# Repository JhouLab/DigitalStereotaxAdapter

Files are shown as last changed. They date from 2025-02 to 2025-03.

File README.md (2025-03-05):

Ridiculously cheap (and functional) 3-axis digital stereotax adapter
============================================

<div align="center">
<video src="https://github.com/user-attachments/assets/23dbc953-8d90-421e-99c2-d5927db93f00" />
</div>

_by Tom Jhou_

---

## Overview:

This project will digitize all three axes of a Stoelting Lab Standard Manipulator Arm, like this one: https://stoeltingco.com/Neuroscience/Standard-Manipulator-Arms~9758

Cost is about \$30 for the AP axis, and $10 for each of the DV and RL axes. These are NOT typos, it really is that
cheap, about 98% less than Stoelting's digital conversion kit. You will also need about \$50-ish in hand tools,
along with a 3D printer and basic familiarity with its use.

Accuracy is 0.01mm in the AP axis (same as Stoelting), and 0.1mm in the DV and RL axes, which is less accurate,
but likely still good enough, as the anatomical variation between animals will exceed this anyway. We've been using
this in our lab since 2024, and it works quite well.

If you have problems, ideas, or comments, contact me at tomjhou@gmail.com or tjhou@som.umaryland.edu.

## Requirements:

1. A 3D printer. Almost any model works, including small tabletop ones like the Bambu A1 mini.
2. About 100 grams of PLA filament (about $3 worth)
3. This 150mm digital readout: ($28.99): https://www.amazon.com/gp/product/B089ZSG84J/ref=ppx_yo_dt_b_search_asin_title?ie=UTF8&th=1
4. Two 6" calipers (<$10 each): READ STEP 1 INSTRUCTIONS BELOW BEFORE YOU BUY: https://www.amazon.com/Digital-Caliper-Adoric-Calipers-Measuring/dp/B07DFFYCXS
5. Any cutting tool, like this one: https://www.amazon.com/Xuron-Model-9180-Kevlar-Scissor/dp/B00068P3TY
6. 6mm long M3 screws + washers, like this (pack of 500, but you only need 2): https://www.amazon.com/HELIFOUNER-Phillips-Screws-Kit-Stainless/dp/B0BV9CF62L
7. Optional (but highly recommended) #8x32-1/4" stainless steel machine screws.<br>
    Pack of 100 screws (but you only need 2): https://www.mcmaster.com/91772A190/<br>
    Tap tool for cutting threads: https://www.amazon.com/Drill-America-DWT54279-High-Speed-Threading/dp/B00DL7COVW<br>
    Manual holder for tap tool: https://www.amazon.com/AUTOTOOLHOME-Drilling-Capacity-0-315-Screwdriver/dp/B01M4FY99G<br>
8. Waterproof glue (e.g. "Amazing Goop", shoe goo, etc) for base clamps. https://www.amazon.com/Amazing-GOOP-140231-Purpose-Clear/dp/B006NTE01M

All links are accurate as of March 2025, but parts on Amazon are subject to change. If any links are broken,
please email me.

Note: the 3D printed parts will fit snugly together. This is by design, to eliminate loose play in the system.
However, this means the tight fits can be disrupted by small differences in 3D printer settings, or by
small manufacturing design changes in Stoelting's components or the digital readouts and calipers.
If any parts don't fit perfectly on your system, please let me know.

Instructions:
=============

## Step 1: Buy the parts listed above.

IMPORTANT: the 6" caliper linked above comes in several varieties.
You MUST get the 6" model (not 8") in BLACK (not red or silver). It has a black plastic body,
with red/yellow/blue buttons. Do NOT buy any of the steel models, as the caliper body/jaws need to be cut
later (see step 3.6 below), and the metal ones are vastly harder to cut.

## Step 2: Print AP axis parts

Print the following two files in the "STL files" folder:

1. "Stoelting AP, parts 1-2 of 4, USE SUPPORTS.stl"
2. One of the following, depending on whether you are converting a left or right arm:<br>
    "Stoelting AP, parts 3-4 of 4, LEFT, NO SUPPORTS.stl"<br>
	"Stoelting AP, parts 3-4 of 4, RIGHT, NO SUPPORTS.stl"

The first file should be printed with supports _enabled_ in your 3D printer settings,
while the second file should be printed _without_ supports enabled (otherwise the holes will fill with PLA, and you will
have to drill them out). This gives you four total parts:

1. Spacer (long flat piece with rectangular slots at both ends)
2. Y-shaped adapter.
3. Base clamp (back corner).
4. Base clamp (side).

OPTIONAL BUT HIGHLY RECOMMENDED: The base clamps have 3.4mm holes in them. You can tap #8-32 theads into these holes,
allowing you to attach a screw for extra stability in step 3.4below. Tapping threads should take only about 60
seconds using cheap hand tools.

<div align="center">
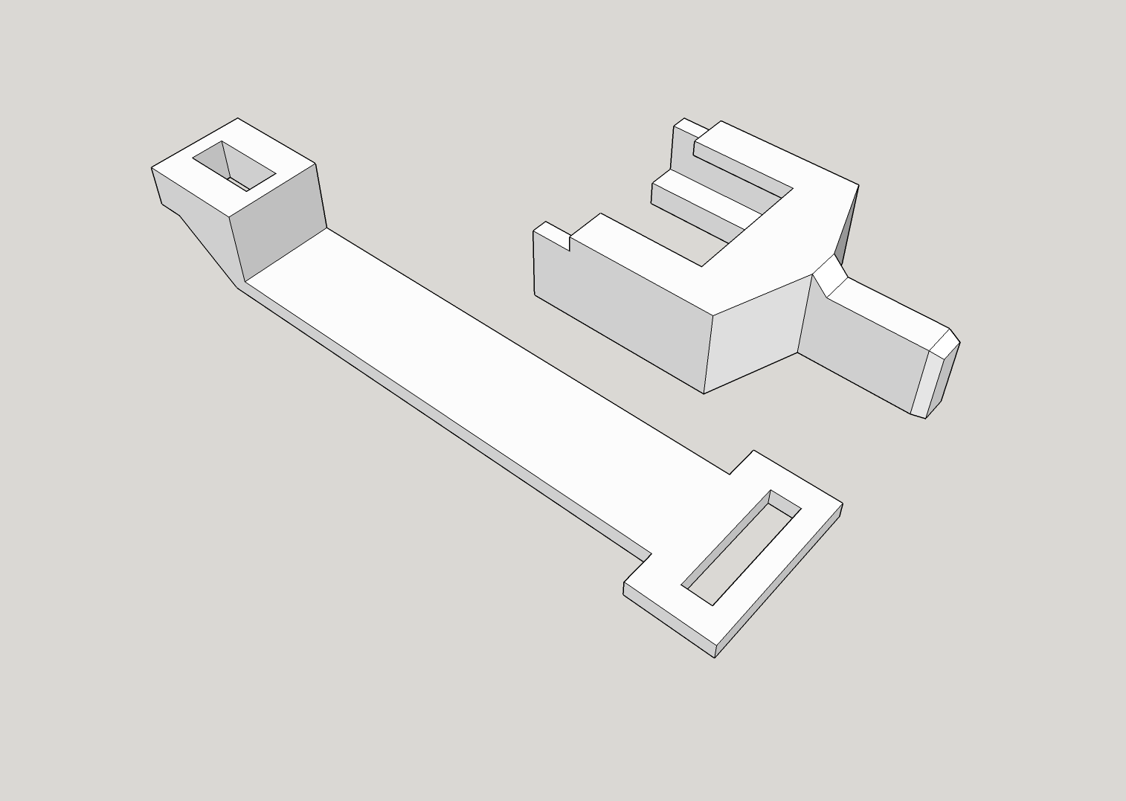
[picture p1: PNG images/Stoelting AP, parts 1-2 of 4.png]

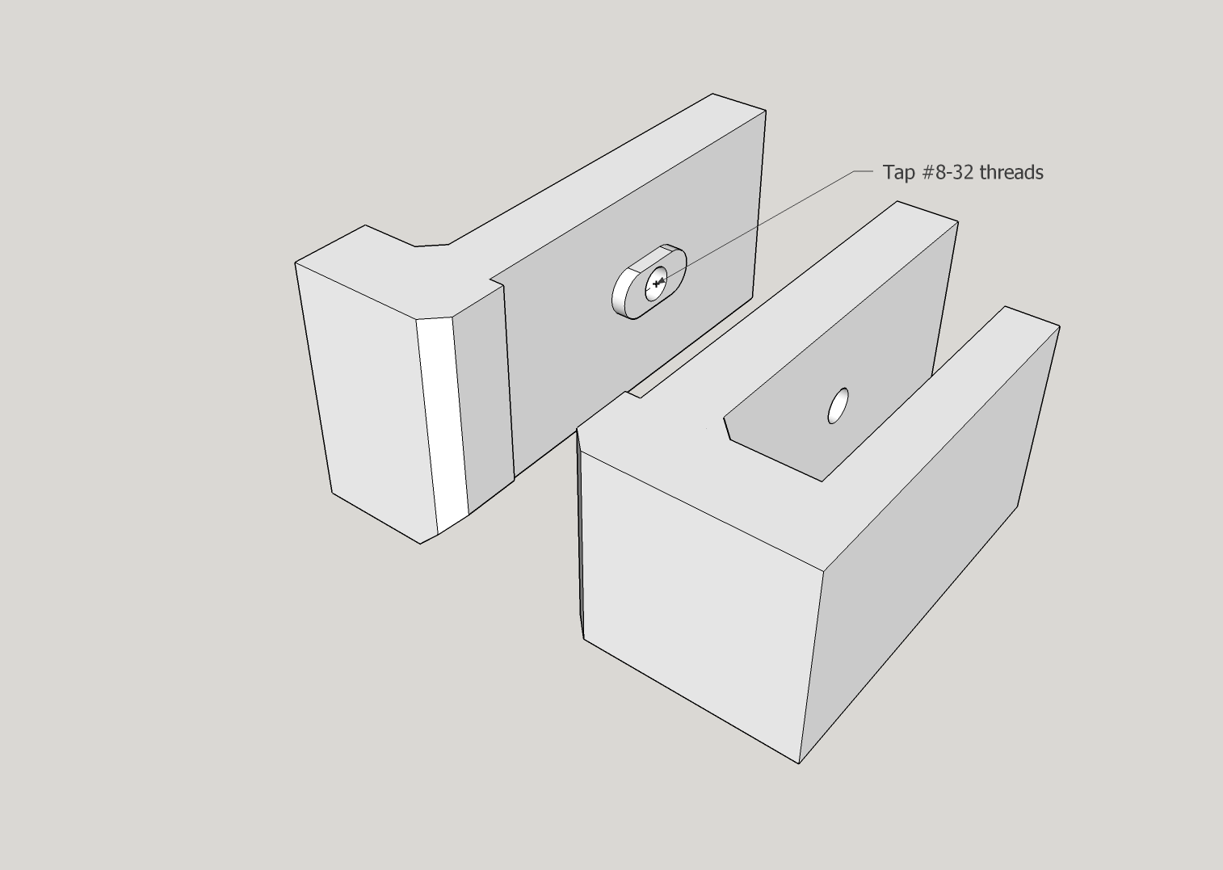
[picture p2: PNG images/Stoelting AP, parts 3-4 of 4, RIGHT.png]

</div>

---

When you print the spacer and Y-shaped adapter, make sure you can fit the stem of the Y-adapter into
the spacer slot. It will likely be hard to insert at first, but with a little pressure it should go in. Once
you verify that they fit, please separate the pieces again and go onto the next step.

<div align="center">
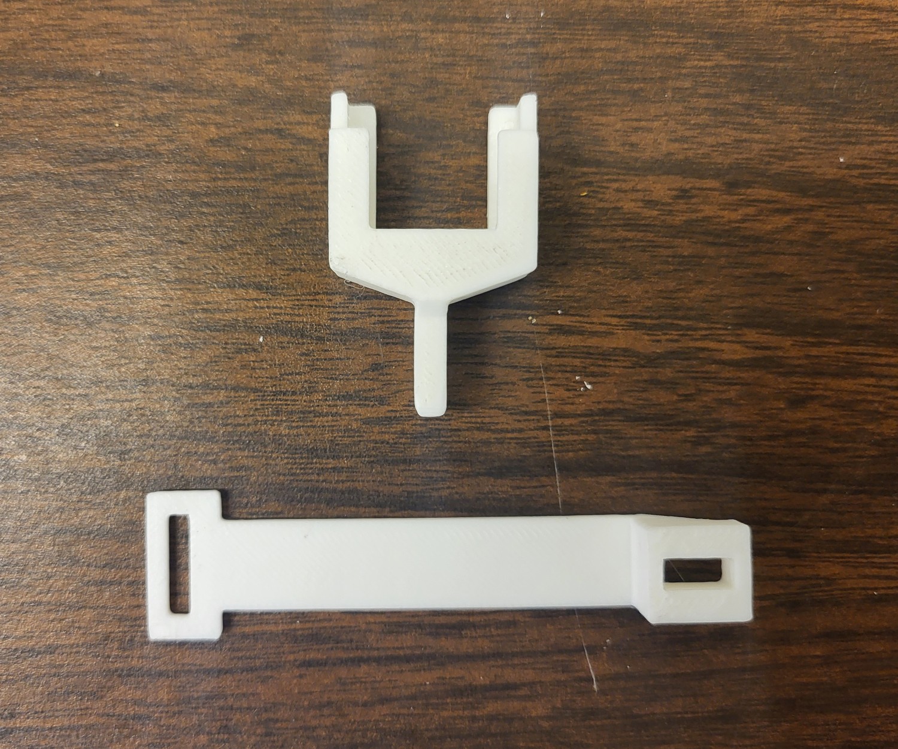
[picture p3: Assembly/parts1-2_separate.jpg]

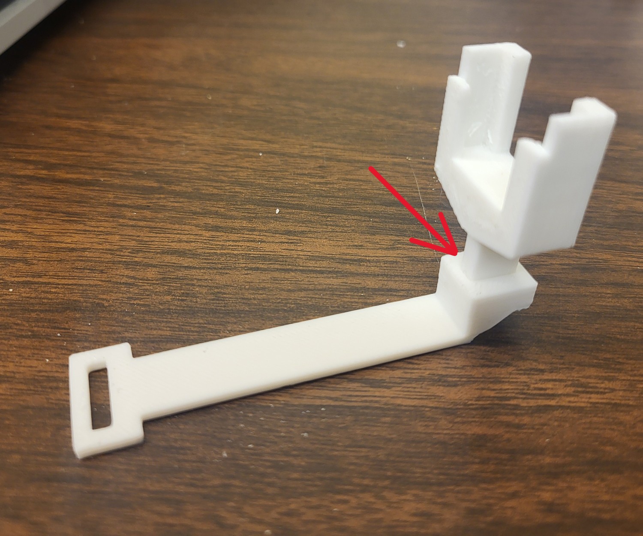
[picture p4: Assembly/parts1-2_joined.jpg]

</div>

## Step 3: Assemble AP axis parts

3.1: The 150mm digital readout has a blue metal bar with two black metal brackets on each end. You first
need to flip their orientation, as shown below:

<div align="center">
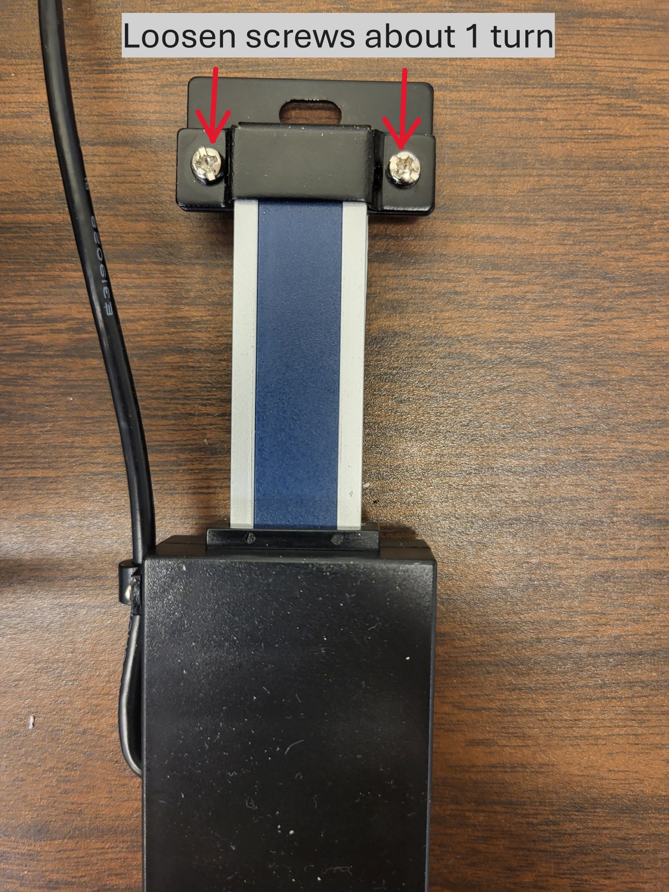
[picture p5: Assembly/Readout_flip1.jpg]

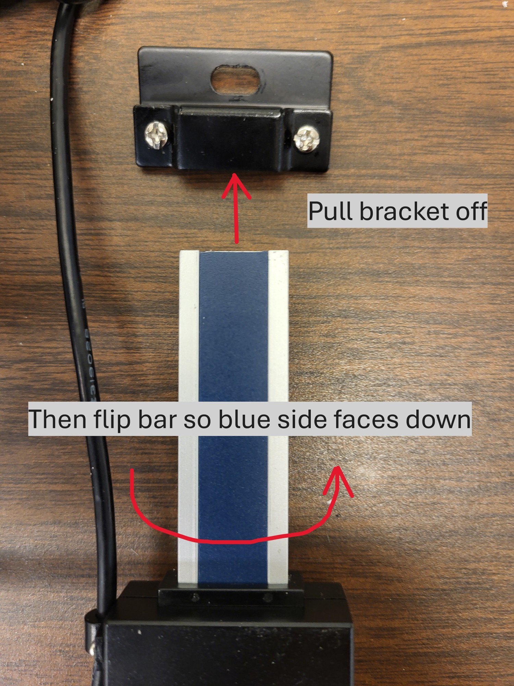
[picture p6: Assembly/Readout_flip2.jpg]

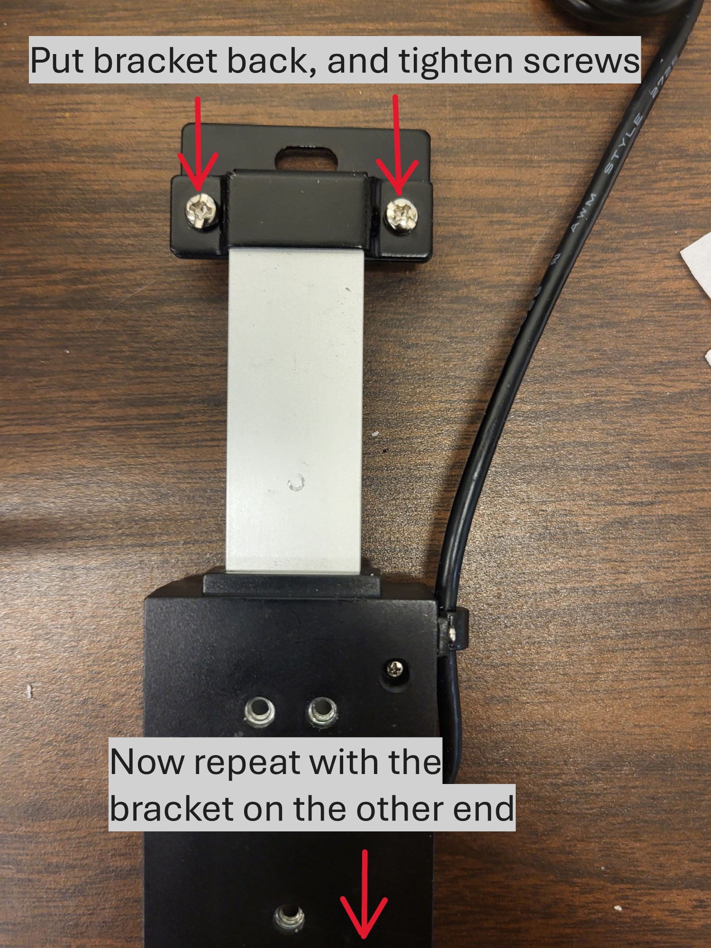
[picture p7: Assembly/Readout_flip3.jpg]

</div>

---
3.2: Attach the spacer to the digital readout using M3 screws and washers:

<div align="center">
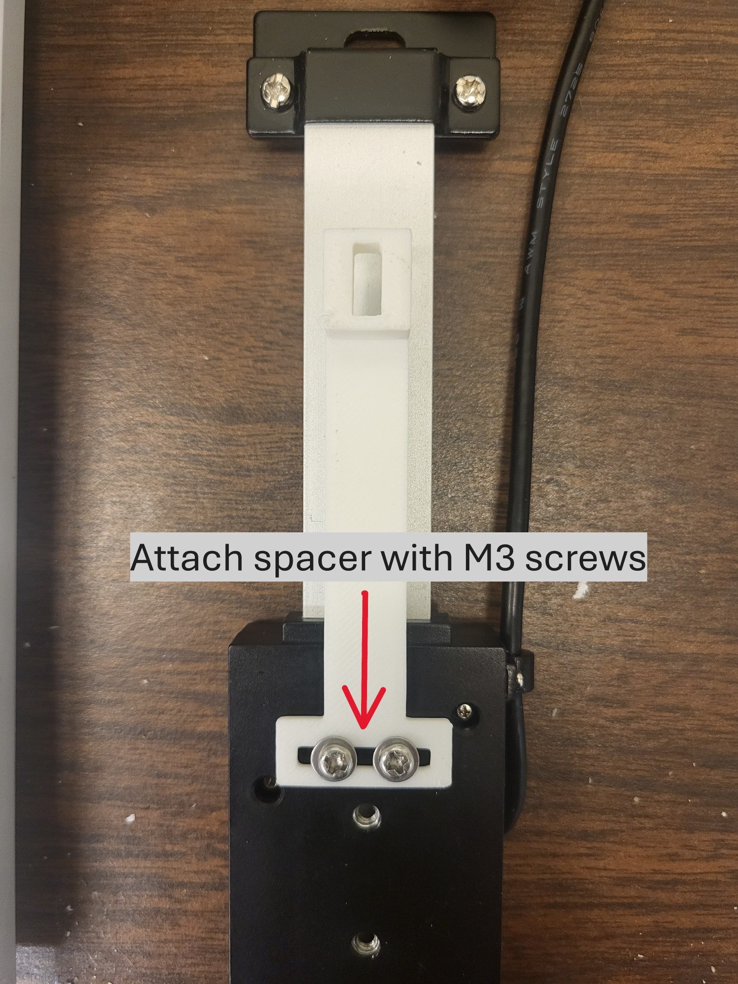
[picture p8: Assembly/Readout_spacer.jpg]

</div>

---
3.3: Slide the Y-shaped piece onto the metal bracket around the knob controlling the AP movement:

<div align="center">
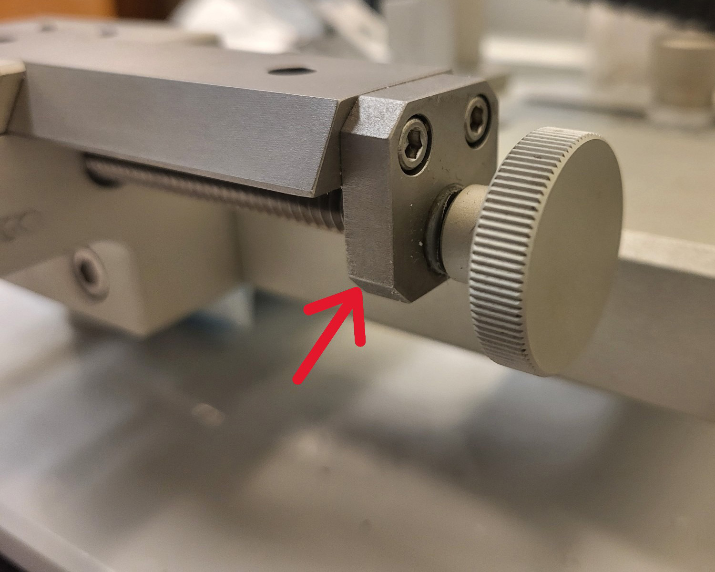
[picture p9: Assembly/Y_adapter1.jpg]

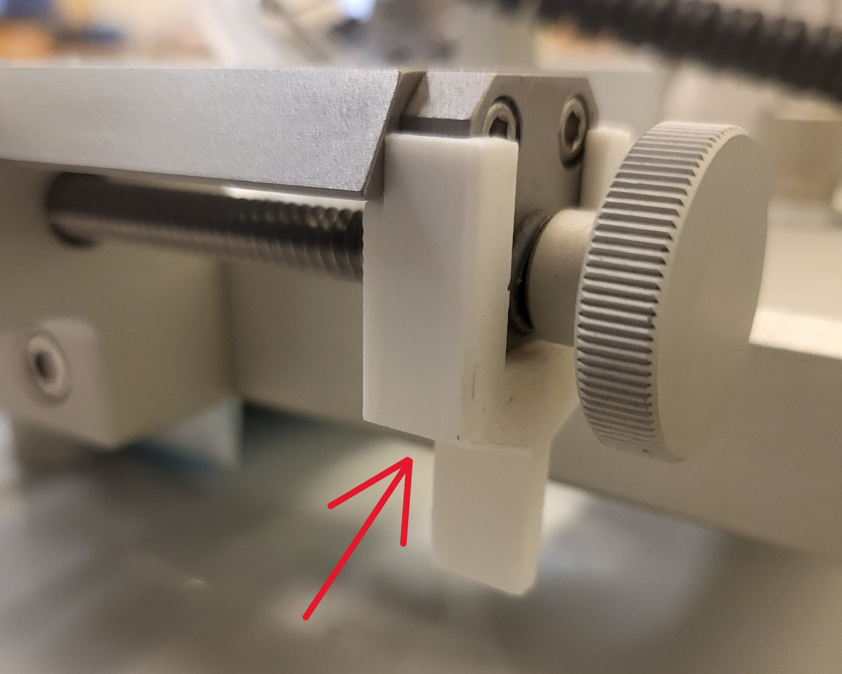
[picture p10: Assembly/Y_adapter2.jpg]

</div>

---

3.4: Place the two base clamps onto the stereotaxic base. One will fit over the back corner, and
the other will slide over the side near the front. Place the digital readout bar on the clamps, aligning the
oval bracket holes with the oval bumps on the clamps.

At this point, the base clamps will be loose, as the metal stereotax base has nothing to lock onto.
To stabilize them, add a couple of drops of glue underneath each clamp to keep it from slipping. I use
"Amazing Goop", a silicone-based glue with stiffening additives, but aquarium glue (which is also silicone-based)
or even krazy glue will work.

If you tapped threads into the holes in the oval bumps, you can now add a 1/4" long #8-32 machine screw to lock
the digital readout bar onto the base clamps. Otherwise, you can use krazy glue or silicone glue to keep the bar
secured to the base clamps.

<div align="center">
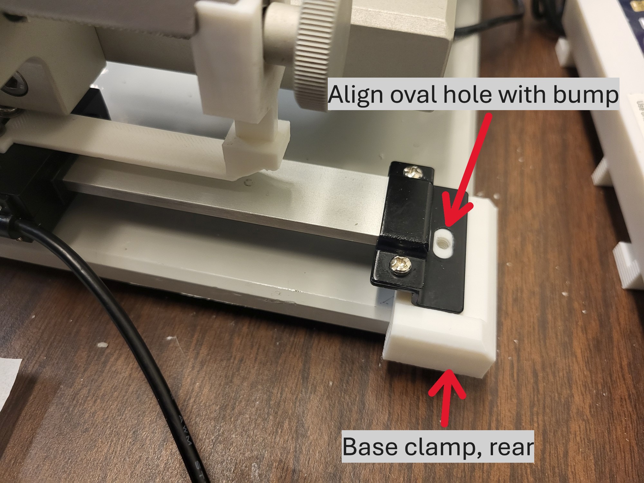
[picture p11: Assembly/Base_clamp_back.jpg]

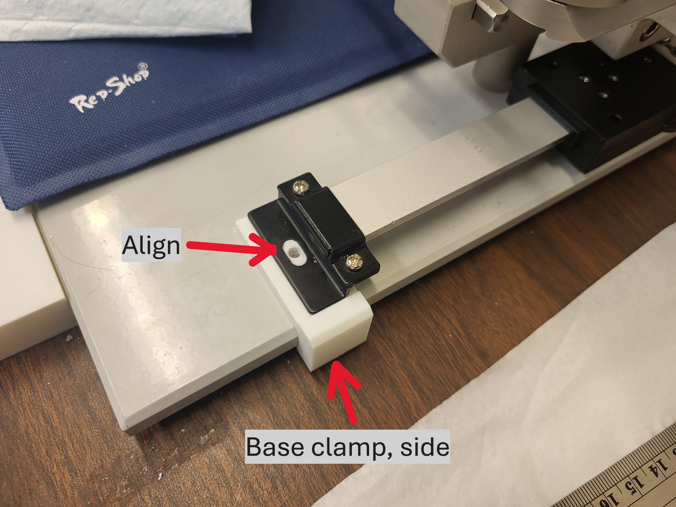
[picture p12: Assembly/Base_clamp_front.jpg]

</div>

---
3.5: Make sure the digital readout slider can slide freely, and then flex the end down slightly and slide it under
the stem of the Y-adapter. Push the spacer end up to lock it to the Y-adapter stem. The fit should be tight:

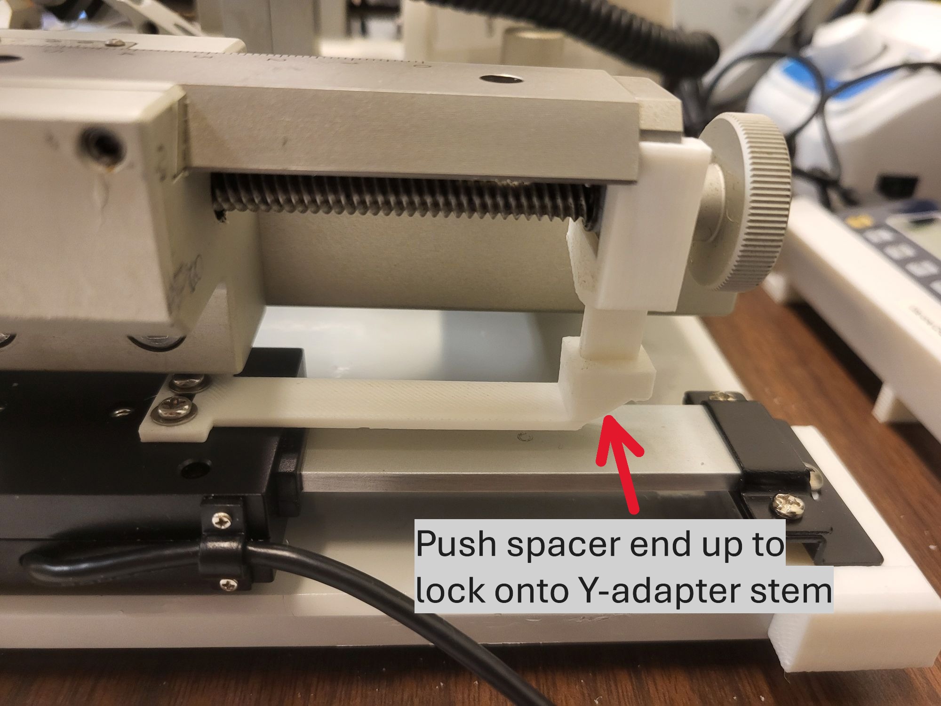
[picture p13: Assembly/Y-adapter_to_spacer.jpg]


---
3.6: OPTIONAL: print the "AP readout panel holder.stl" file, and snap the digital readout panel into the pocket.
The cable tucks underneath the holder.

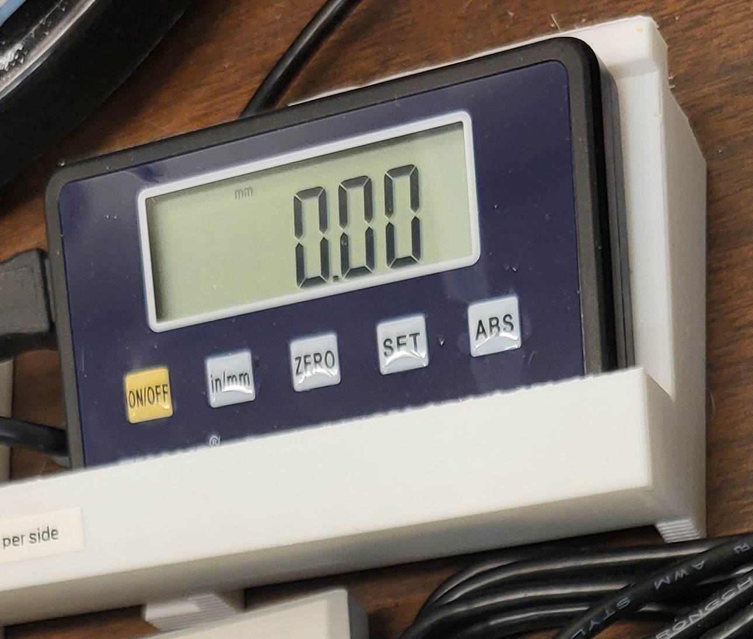
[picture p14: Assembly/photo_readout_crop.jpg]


## Step 4: Print RL and DV axes parts:

Each of the RL and DV axes has two files (one labeled "caliper body" and one labeled "knob clamp"). There are separate
arms for the right and left arms, hence 2 x 2 x 2 = 8 files total.

You can print the files in any order, and you should print only the ones you need, e.g. if you are converting a left
arm, you do not need to print the right side parts.

Supports should be ENABLED in your 3D printer for these parts. Make sure to track which part is which, as
they are NOT interchangeable, despite looking very similar.

Drawings of parts for right DV axis:
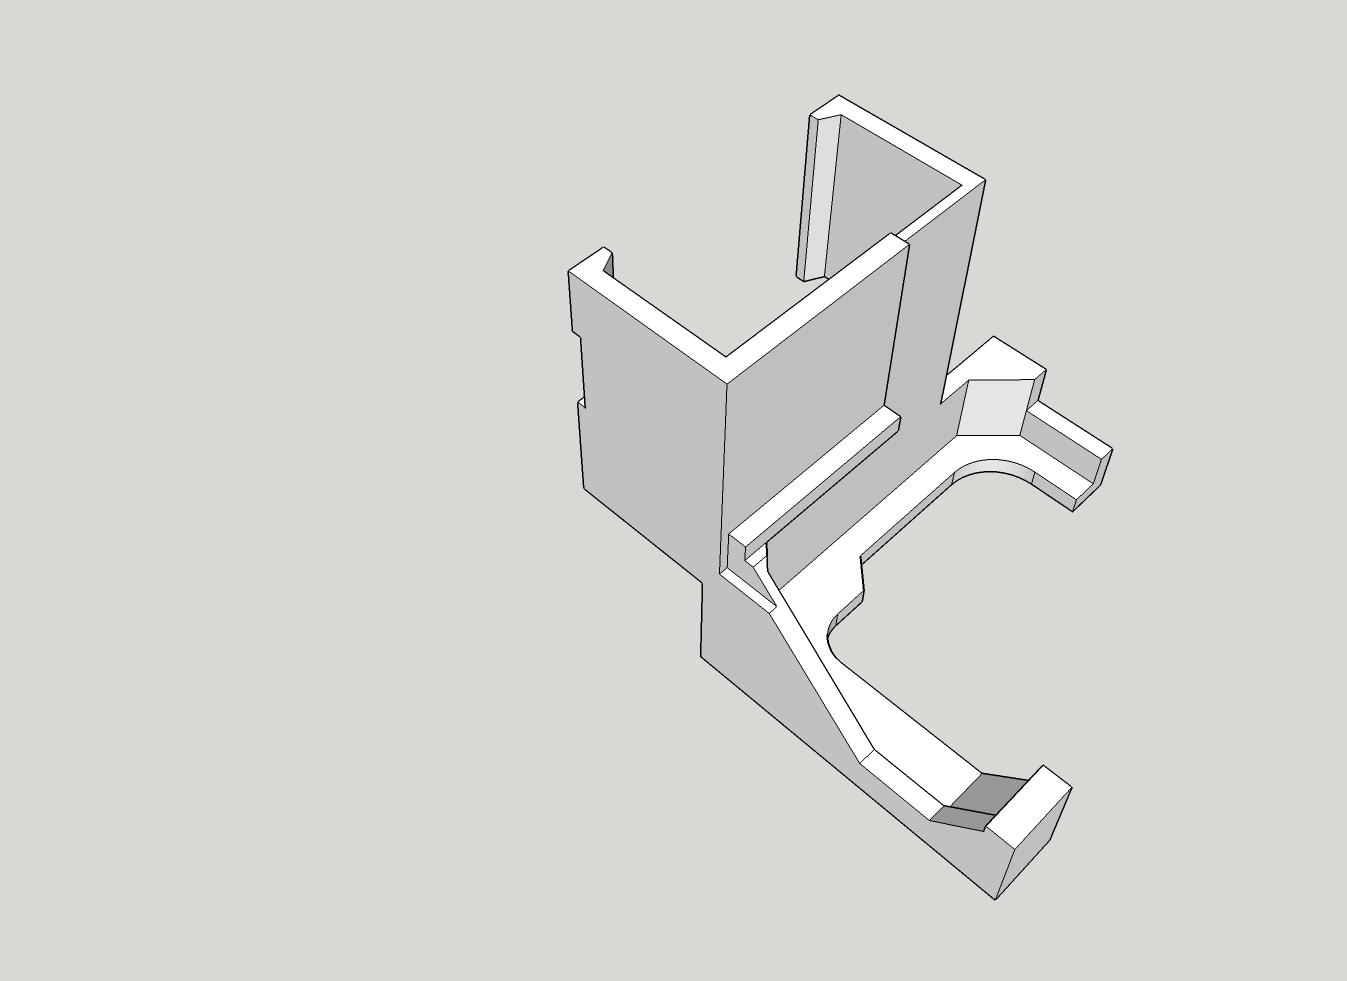
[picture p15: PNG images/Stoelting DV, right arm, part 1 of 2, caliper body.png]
<div align="center">
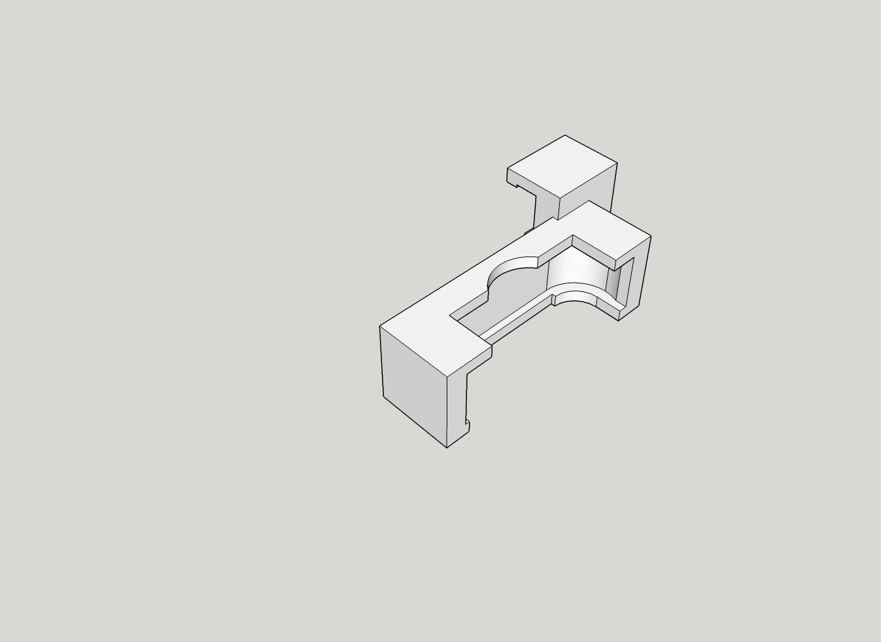
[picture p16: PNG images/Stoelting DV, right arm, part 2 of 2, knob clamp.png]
</div>

## Step 5: Snap RL and DV axes clamps onto arm:

The parts labeled "knob clamp" will snap onto the oval-shaped metal piece just below each knob. The parts labeled
"caliper body" should snap onto the central block of the arm. Without a video, it is hard to describe exactly how
to orient these parts. But you should be able to see their orientation from the photo below. As usual, the fit will be snug.

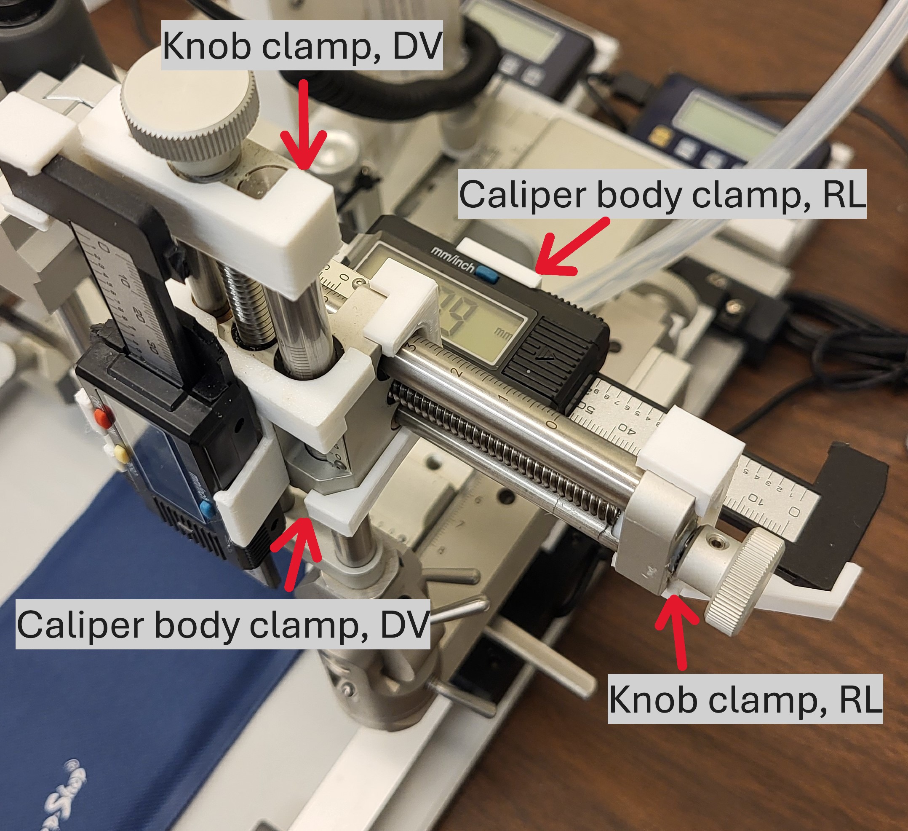
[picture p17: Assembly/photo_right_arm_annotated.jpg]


## Step 6: Cut the caliper jaws and ruler, and snap it onto arm:

The calipers each come with a long "ruler" that extends about a foot. Cut off the part past
about 140mm. The plastic is soft, and should cut without too much difficulty. If you are a few millimeters
too long or short, it is fine, the exact length is not critical.

There is also a central "spindle" that will protrude as you open/close the caliper. Cut that off too as far as you can.
You might have to slide the body almost to the end to fully remove the spindle. There are some small plastic pieces
inside the body that might fall out when you do this. Don't worry, they aren't necessary to keep.

Finally, completely remove 3 of the caliper jaws, while removing half of the  one half intact, as shown below:

<div align="center">
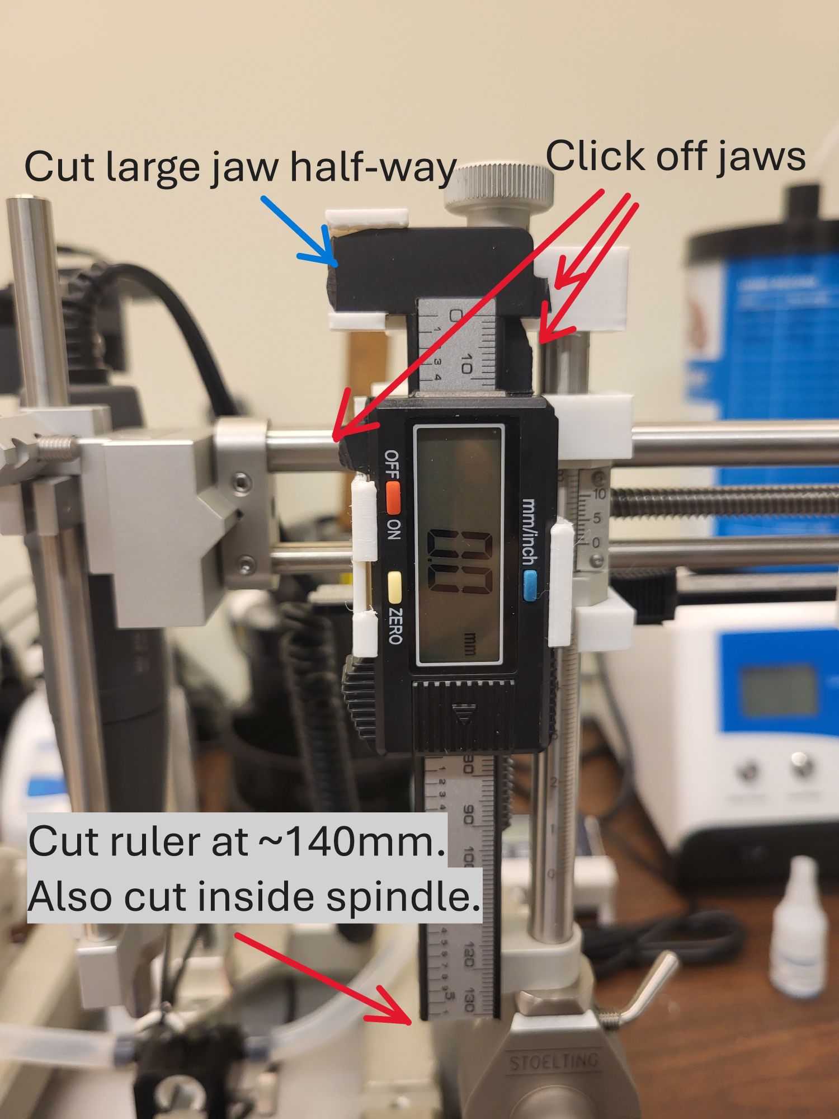
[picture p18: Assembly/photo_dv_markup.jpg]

</div>
<div align="center">
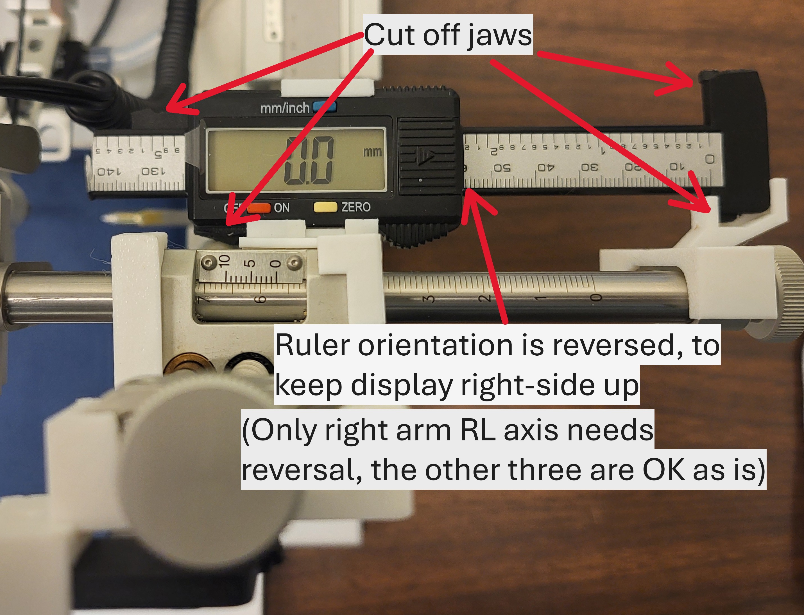
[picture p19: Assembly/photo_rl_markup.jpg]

</div>

Snap the caliper into the 3D-printed clamps, as in the photos. This might take some trial and error, and patience.

That should be it. As you can see, this is not an easy project, I myself had to print and assemble these parts
several times before I got everything right.

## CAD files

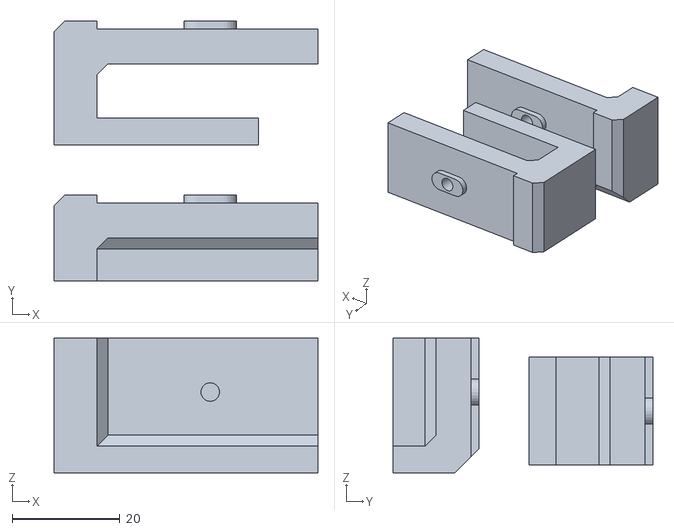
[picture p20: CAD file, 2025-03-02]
STL files/Stoelting AP, parts 3-4 of 4, LEFT, NO SUPPORTS.stl
49.0 x 48.3 x 25.0

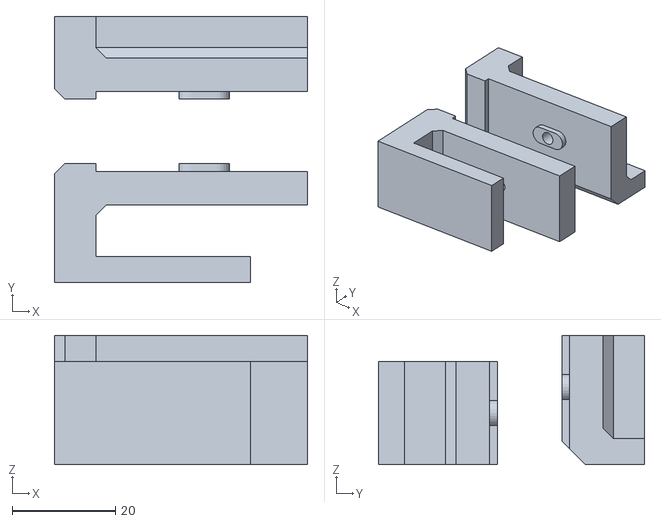
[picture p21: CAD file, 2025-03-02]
STL files/Stoelting AP, parts 3-4 of 4, RIGHT, NO SUPPORTS.stl
49.0 x 51.5 x 25.0

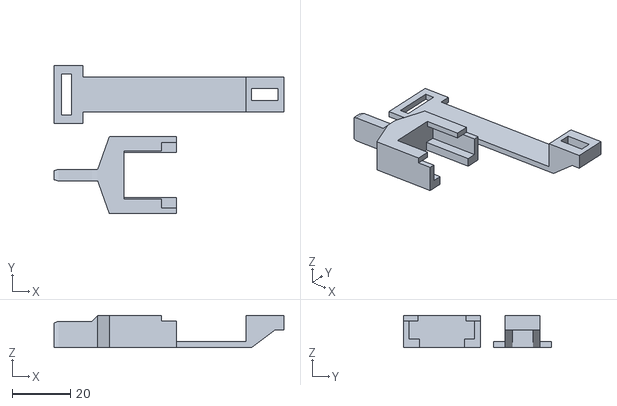
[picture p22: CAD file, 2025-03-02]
STL files/Stoelting AP, parts 1-2 of 4, USE SUPPORTS.stl
79.0 x 51.0 x 11.0

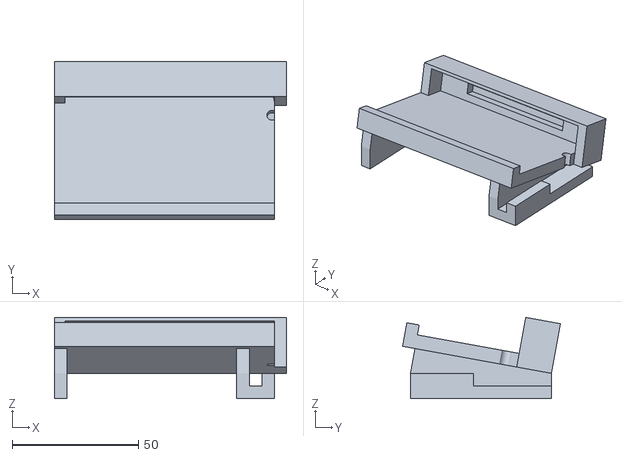
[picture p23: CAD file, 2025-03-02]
STL files/AP readout panel holder.stl
92.0 x 62.6 x 32.2

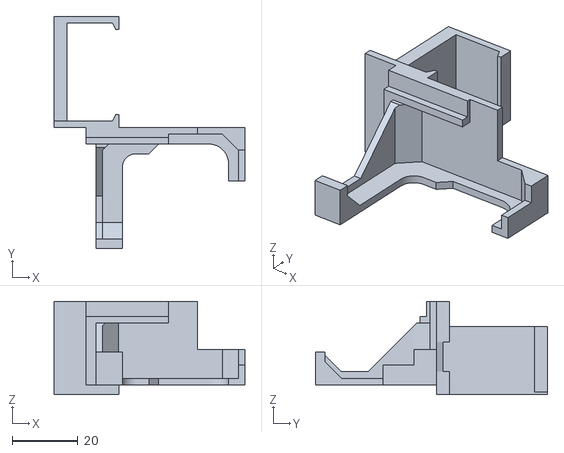
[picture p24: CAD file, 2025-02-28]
STL files/Stoelting RL, right arm, part 1 of 2, caliper body clamp.stl
58.1 x 70.6 x 28.4

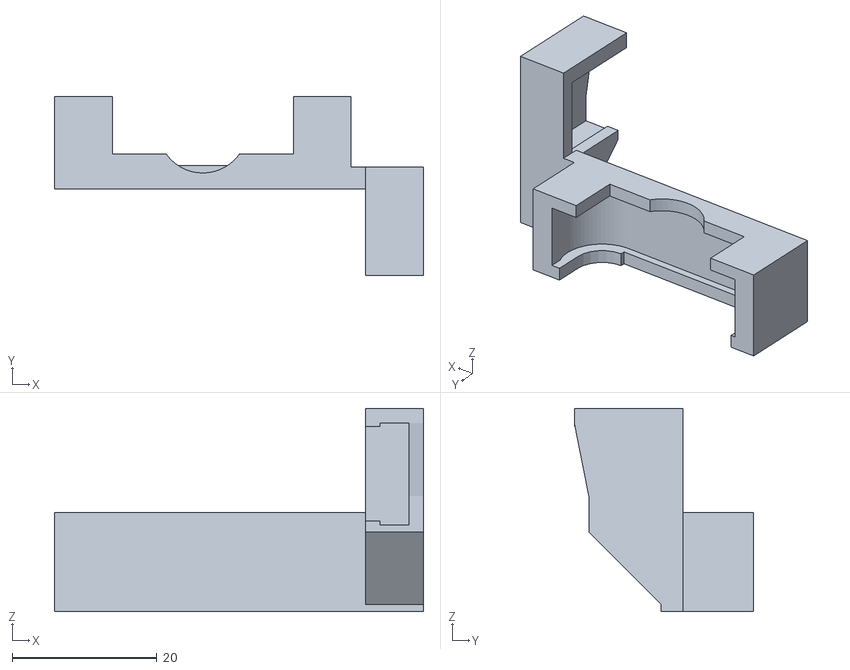
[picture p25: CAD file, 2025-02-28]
STL files/Stoelting RL, left arm, part 2 of 2, knob clamp.stl
51.0 x 24.8 x 28.1

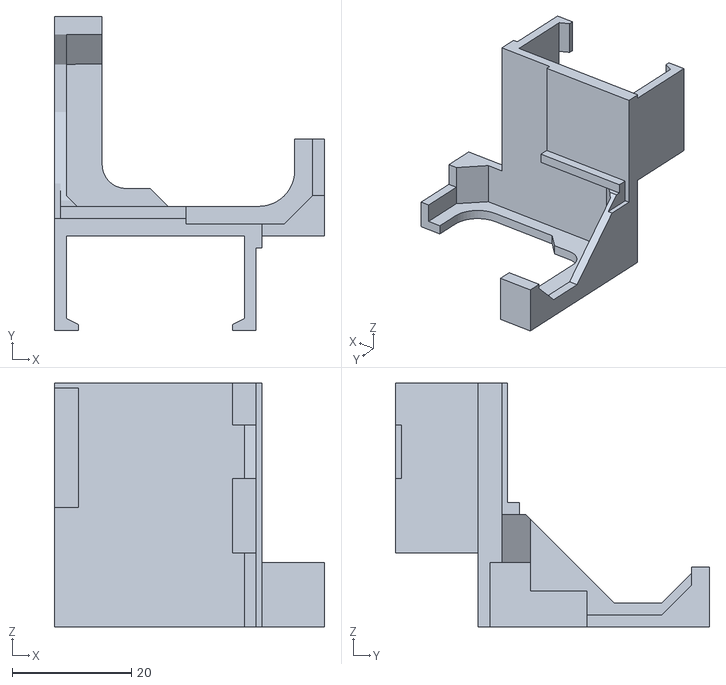
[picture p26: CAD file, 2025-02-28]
STL files/Stoelting DV, left arm, part 1 of 2, caliper body clamp.stl
45.2 x 52.6 x 40.8

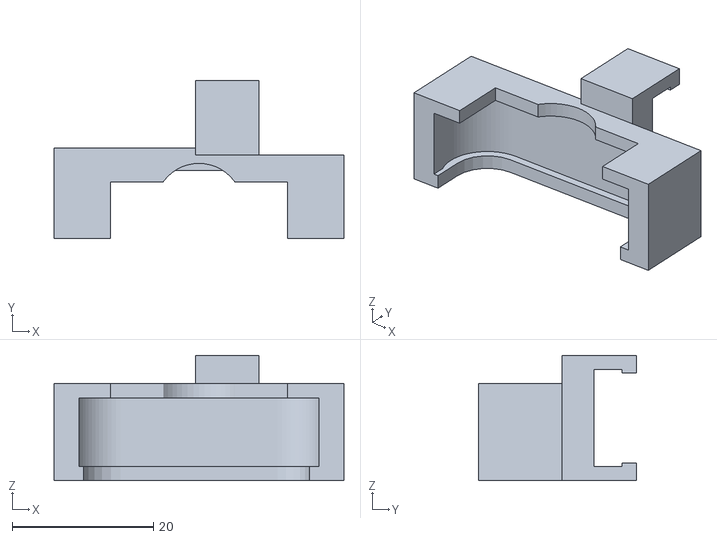
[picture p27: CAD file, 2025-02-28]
STL files/Stoelting DV, left arm, part 2 of 2, knob clamp.stl
41.0 x 22.3 x 17.7

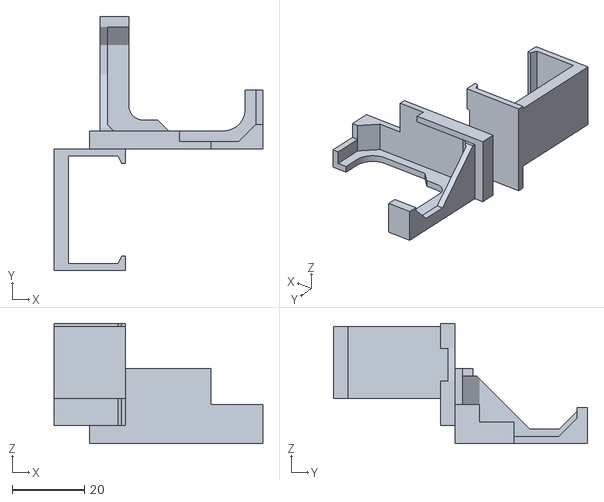
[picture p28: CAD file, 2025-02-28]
STL files/Stoelting RL, left arm, part 1 of 2, caliper body clamp.stl
58.1 x 70.6 x 33.4

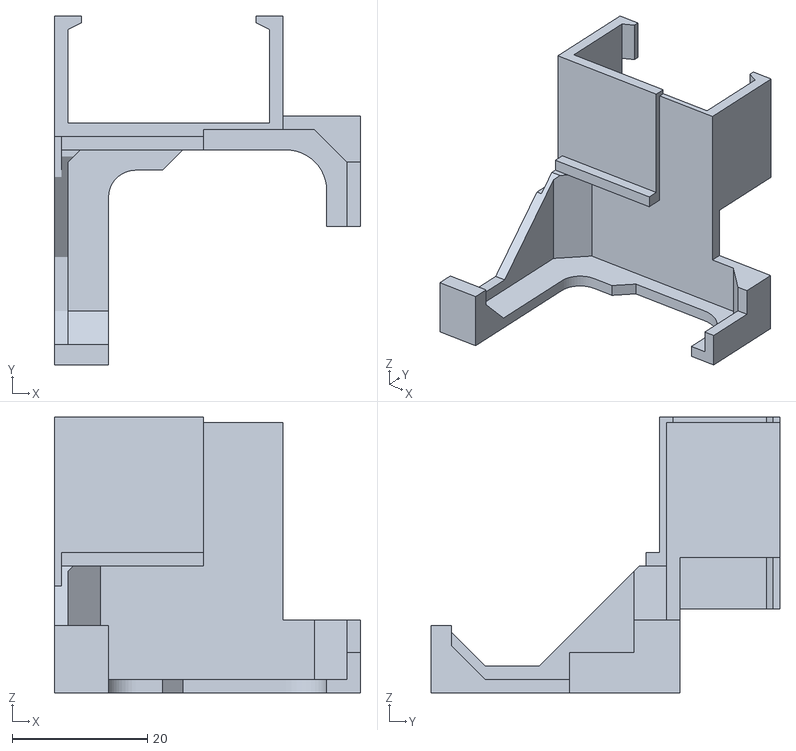
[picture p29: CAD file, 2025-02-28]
STL files/Stoelting DV, right arm, part 1 of 2, caliper body clamp.stl
45.2 x 51.6 x 40.8

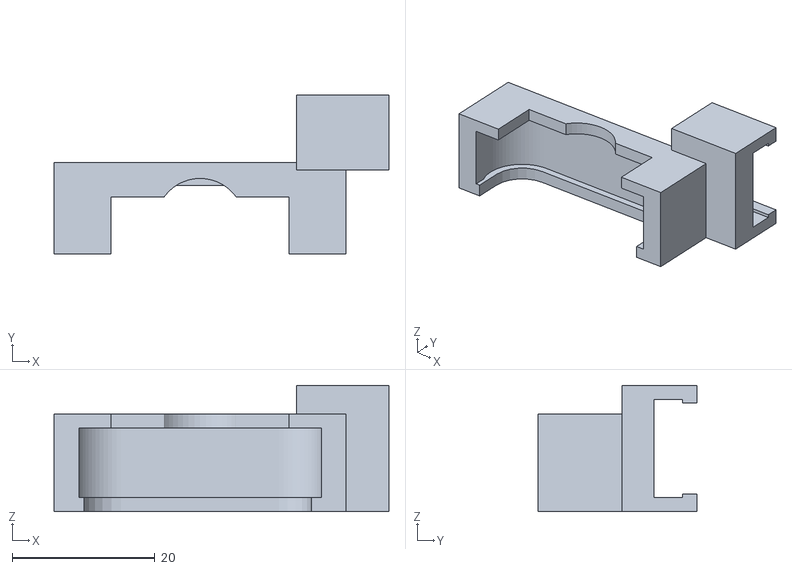
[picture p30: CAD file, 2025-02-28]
STL files/Stoelting DV, right arm, part 2 of 2, knob clamp.stl
47.0 x 22.3 x 17.7

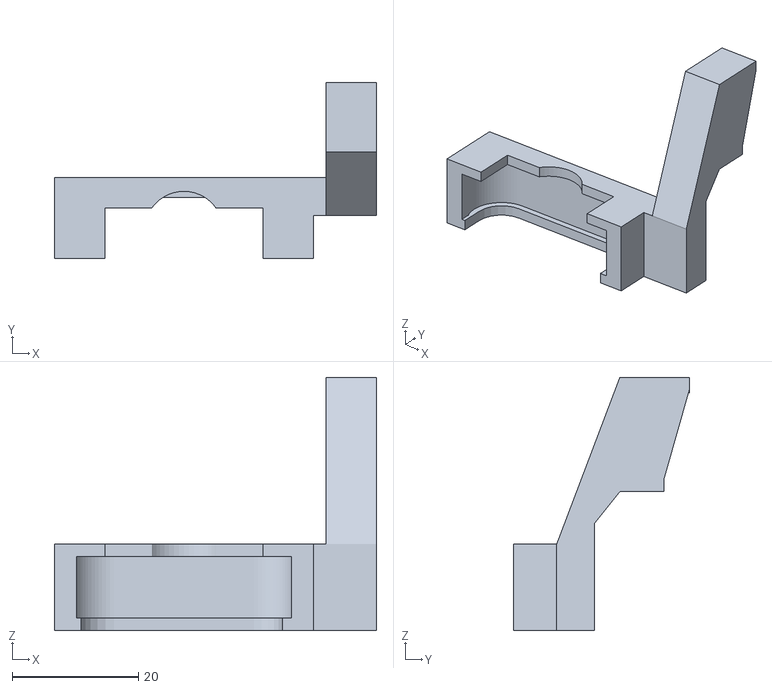
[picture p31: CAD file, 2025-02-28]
STL files/Stoelting RL, right arm, part 2 of 2, knob clamp.stl
51.0 x 27.8 x 40.1

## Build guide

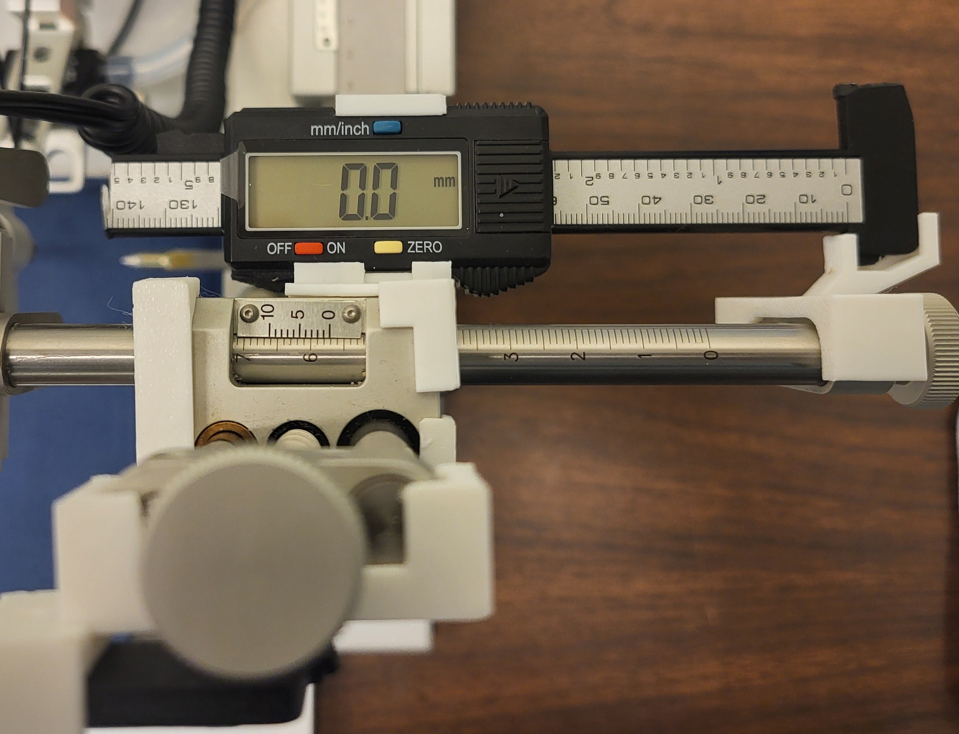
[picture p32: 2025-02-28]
Assembly/photo_rl.jpg

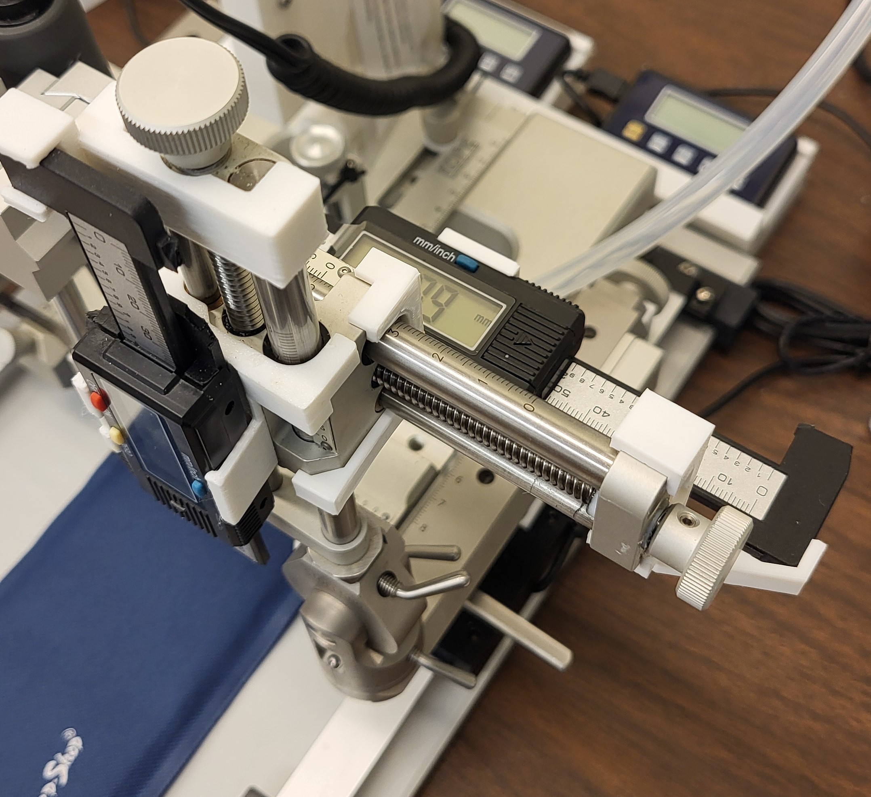
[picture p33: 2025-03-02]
Assembly/photo_right_arm.jpg

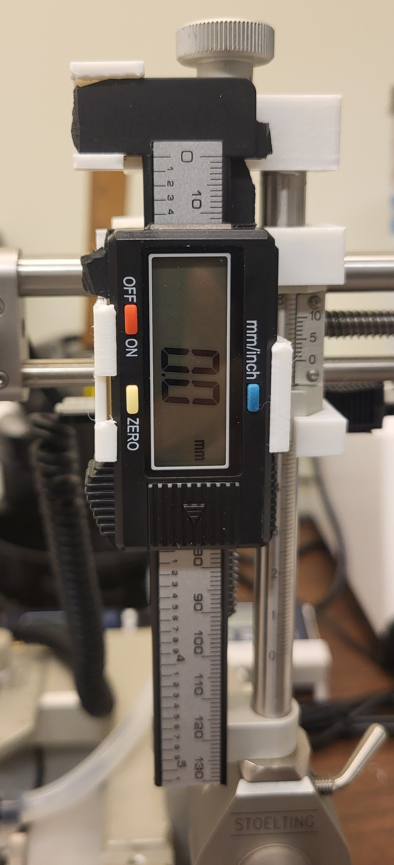
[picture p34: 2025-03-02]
Assembly/photo_dv.jpg

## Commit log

2025-02-28 Added STL files
    [Stoelting AP, part 1 of 2, left side.stl, Stoelting AP, part 1 of 2, right side.stl, Stoelting AP, part 2 of 2, either side.stl, Stoelting DV, left arm, part 1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]
2025-03-02 Updated instructions and STL files, added more photos
    [AP readout panel holder_dual.stl, Consolidated AP left.stl, Consolidated AP right.stl, Stoelting AP, part 1 of 2, left side.stl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]
2025-03-02 Updated PNG filenames from "knob" to "knob clamp", to match STL
2025-03-02 Added photo of AP readout panel
    [AP readout panel holder.stl, AP readout panel holder_dual.stl]
2025-03-02 Added instructions for flipping readout bar bracket
2025-03-02 Added photos of base clamp, updated stl files for AP axis
    [Consolidated AP left.stl, Consolidated AP right.stl, Stoelting AP, parts 1-2 of 4, USE SUPPORTS.stl, Stoelting AP, parts 3-4 of 4, LEFT, NO SUPPORTS.stl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]
